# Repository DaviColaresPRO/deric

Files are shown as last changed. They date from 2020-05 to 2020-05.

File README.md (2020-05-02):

# deric - Desenvolvimento Experimental de Física Colaborativo
Sabe-se que não é fácil introduzir os jovens no mundo científico, mas existem maneiras de facilitar esse processo. Uma delas é a participação em olimpíadas científicas, e um bom exemplo é a OBF (Olimpíada Brasileira de Física). Em sua última fase, a OBF conta com uma prova teórica e uma prova experimental, cada uma valendo quase metade da nota final. Para conseguir um bom resultado, é essencial que o estudante vá bem em ambas. Porém, poucas são as escolas que possuem uma boa preparação em física experimental no país, pois é necessário contar com kits experimentais variados e com as instruções de como usá-los da maneira correta. É aí que o Projeto deric age, na democratização do acesso a equipamentos de laboratório e no ensino do uso eficiente destes. O projeto pretende alcançar o seu objetivo através da disponibilização na internet (no site GitHub) de guias de montagem e de utilização de kits experimentais de baixo custo, sendo o MDF a principal matéria-prima. Além disso, a plataforma GitHub permite que qualquer pessoa modifique e redistribua o material em diferentes versões, permitindo que os materiais sejam adaptados a diferentes demandas. Vários desses kits já foram usados no treinamento de uma escola de Fortaleza, contribuindo para o seu alto desempenho na OBF e na seletiva para as olimpíadas internacionais de física. Assim sendo, os kits se mostraram efetivos. Vale notar também que esses equipamentos podem ser usados para melhorar a didática em sala de aula, já que experimentos visuais facilitam o aprendizado.
- Projeto desenvolvido por Davi Colares: https://www.linkedin.com/in/davi-colares/, Davi Maciel: linkedin

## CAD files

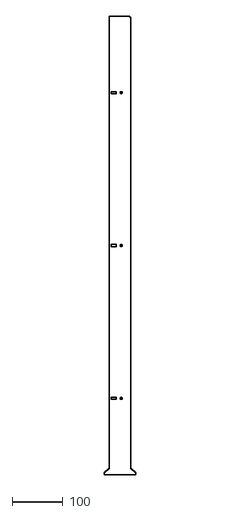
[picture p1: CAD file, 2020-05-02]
Experimentos de Física/Viscosímetro de Stokes/Arquivos dxf/Suporte Lateral.dxf
62.0 x 900.0

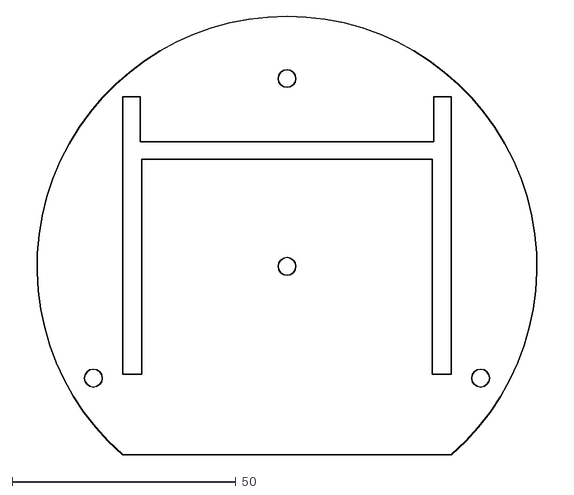
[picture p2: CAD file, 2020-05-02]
Experimentos de Física/Viscosímetro de Stokes/Arquivos dxf/Base do Suporte.dxf
121.0 x 98.0

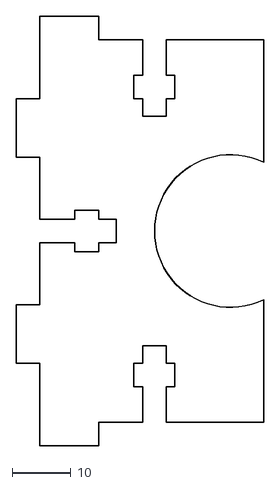
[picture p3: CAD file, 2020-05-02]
Experimentos de Física/Viscosímetro de Stokes/Arquivos dxf/Suporte da Lâmpada (x3).dxf
42.1 x 73.0

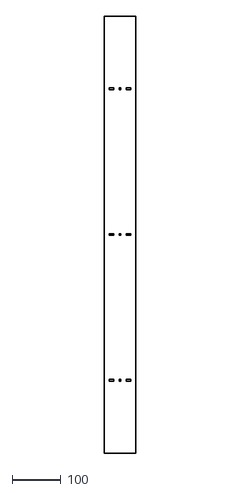
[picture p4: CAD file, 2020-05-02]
Experimentos de Física/Viscosímetro de Stokes/Arquivos dxf/Suporte Frontal.dxf
65.0 x 900.0

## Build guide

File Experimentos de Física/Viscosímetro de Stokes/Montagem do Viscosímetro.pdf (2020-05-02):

# Viscosímetro de Stokes

Davi Colares - Manual de Montagem

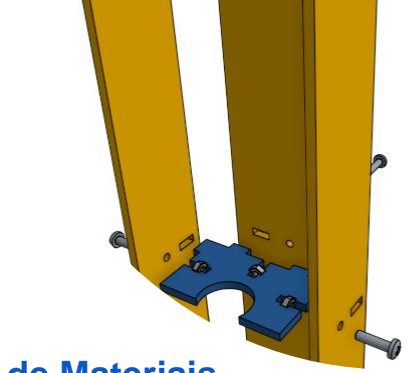
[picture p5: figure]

## Lista de Materiais

- Peças cortadas em MDF ou Acrílico
- 9 Parafusos M4X16
- 9 Roscas M4
- Uma base para fixar o modelo
- Supercola
- Lixa d’Agua
- Lâmpada de tudo
- Material de proteção
- Alicate
- 4 Parafusos para Madeira M4 (Opcionais)

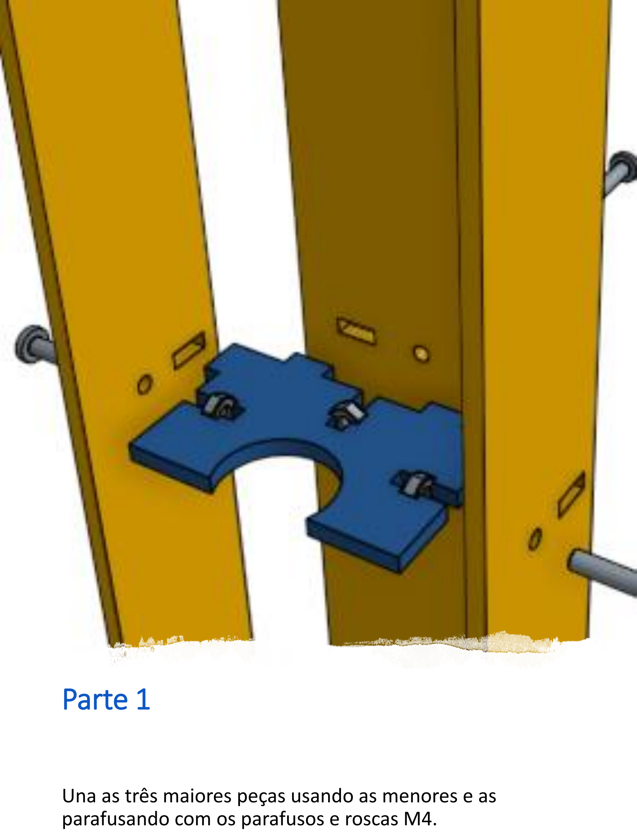
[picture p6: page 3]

## Parte 1

Una as três maiores peças usando as menores e as parafusando com os parafusos e roscas M4.

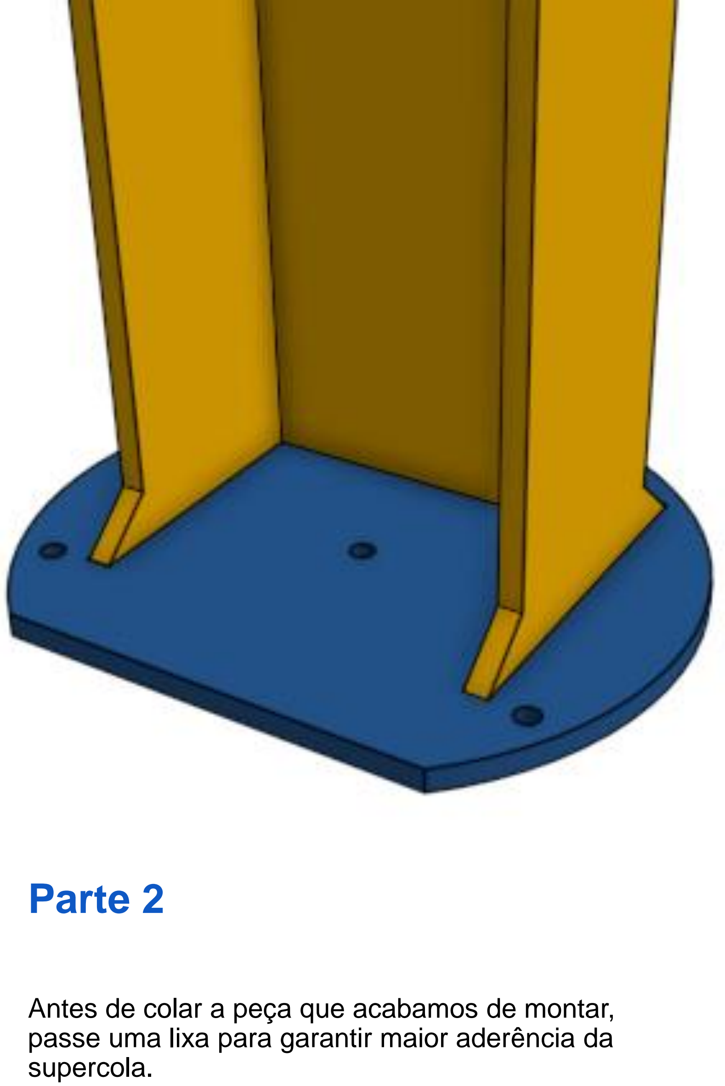
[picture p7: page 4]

## Parte 2

Antes de colar a peça que acabamos de montar, passe uma lixa para garantir maior aderência da supercola.

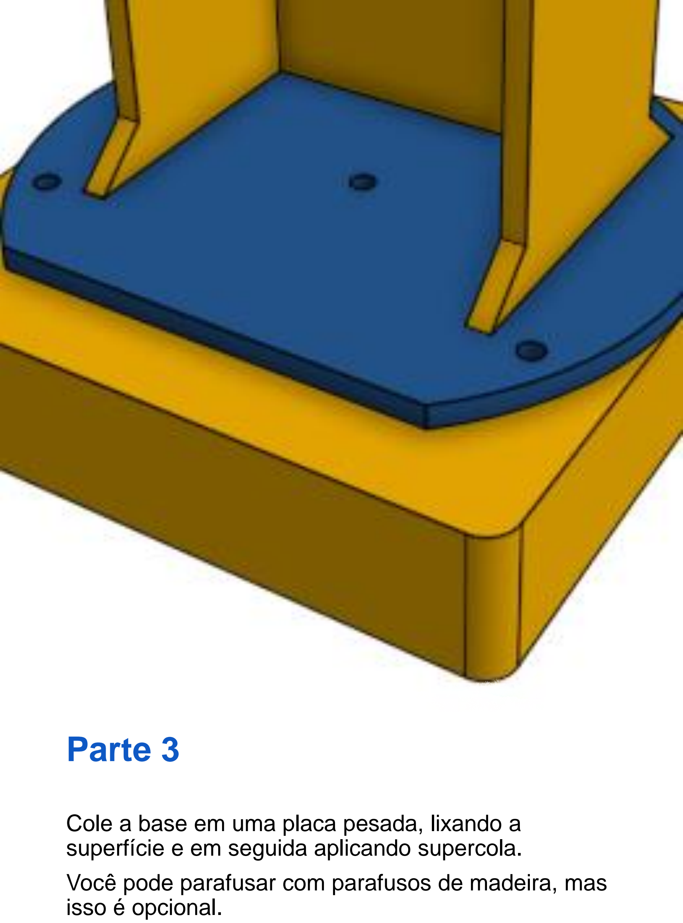
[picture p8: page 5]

## Parte 3

Cole a base em uma placa pesada, lixando a superfície e em seguida aplicando supercola.
Você pode parafusar com parafusos de madeira, mas isso é opcional.

## Suporte Pronto

## Parte 4

Usando material de proteção, iremos abrir o bulbo da lâmpada forçando com um alicate. Dentro de lâmpadas fluorescentes podem ser encontrados gases como argônio e vapor de mercúrio, sendo o último tóxico, além do material de segurança realize a abertura em local arejado.
Após abrir a lâmpada, retire seu conteúdo usando uma chave de fenda ou uma vareta, e lave o interior com água.
Tampe um dos lados usando uma rolha de silicone, ou algum outro material que impeça o vazamento do líquido que será usado na experimental.

## Parte 5

Com o tubo preparado e a cola seca, podemos encaixá-lo na base. Encaixe-o por cima, e nunca de frente, se você perceber que não está encaixando como deveria, então lixe os encaixes e tente novamente, esses tubos são sensíveis e não devem ser forçados contra o suporte.

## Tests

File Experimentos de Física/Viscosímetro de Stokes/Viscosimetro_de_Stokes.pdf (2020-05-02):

## MEDIDA DA VISCOSIDADE DA AGUA ´

Davi MacielaaaaaaaaVers˜ao: 20 de abril de 2020

### 1 Apresenta¸c˜ao e objetivos

Est´a pr´atica experimental tem como objetivo analisar a interferˆencia da viscosidade de um fluido no movimento de um corpo. Vamos estudar as consequˆencias e parˆametros relevantes num sistema simples: o viscos´ımetro de Stokes.

### 2 Materiais

- 1 Suporte para a lˆampada
- 1 Lˆampada preenchida com ´agua
- 1 Fita m´etrica
- 1 Cronˆometro
- Esferas de raios variados
- 1 Im˜a

### 3 Fundamenta¸c˜ao te´orica

A viscosidade ´e a resistˆencia que um fluido apresenta ao escoamento. Para ilustrar, pense numa garrafa com ´agua e numa garrafa com mel. Se vocˆe virar as duas de cabe¸ca pra baixo, ver´a que existe uma maior dificuldade de derramar mel do que derramar ´agua. Isso acontece por que o mel ´e mais viscoso do quˆe a ´agua. A seguir, vamos analisar como essa viscosidade influˆencia a queda vertical de uma esfera homogˆenea na ´agua. Para isso, iremos fazer uso da Lei de Stokes, que relaciona a for¸ca de fric¸c˜ao sentida pela esfera com seus parˆametros e com o meio, quando o n´umero de Reynolds ´e menor que 1. Essa lei ´e descrita pela seguinte f´ormula:

F~ = −6πrη~v,

onde:

F~ ´e a forca de fric¸c˜ao,
r ´e o raio da esfera,
η ´e o coeficiente de viscosidade do fluido, e
~v ´e a velocidade da esfera em rela¸c˜ao ao fluido.

Existem 3 for¸cas agindo na esfera enquanto ela cai na ´agua:

F

E

mg

Figura 1

onde:
F~ ´e a for¸ca de fric¸c˜ao
E~ ´e a for¸ca de empuxo, e m~g ´e o peso.

A 2a Lei de Newton fica:

m~a = m~g + F~ + E~ →

→ ma = mg − 6πrηv − ρaV g,

onde m e V s˜ao a massa e o volume da esfera, respectivamente, e ρa ´e a densidade da ´agua.
Sabendo a densidade ρ da esfera, temos:

m = ρV = ρ

4
3

πr³

Da´ı:

ma = (ρ − ρa)

4
3

πr³
g − 6πrηv.

A velocidade vai aumentando at´e que o lado direito da equa¸c˜ao acima tenda a zero, fazendo que a acelera¸c˜ao tenda a zero da mesma forma. No nosso experimento, podemos considerar que isso acontece bem r´apido, ou seja, vocˆe pode considerar que a esfera come¸ca um movimento uniforme poucos cent´ımetros abaixo da superf´ıcie da ´agua. Assim, a velocidade terminal ´e:

v = (ρ − ρa)

2g
9η

r

2

Com essa rela¸c˜ao em m˜aos e utilizando dados experimentais, podemos achar o coeficiente de viscosidade da ´agua. Podemos achar at´e mesmo o raio de uma esfera, se tivermos o coeficiente de viscosidade da ´agua.

### 4 Procedimentos experimentais

4.1

Utilizando os equipamentos fornecidos, levante dados de deslocamento por tempo de queda para cada esfera, lembrando de esperar que a esfera tenha entrado alguns cent´ımetros na ´agua antes de iniciar a contagem do cronˆometro. Fa¸ca isso 3 vezes para cada esfera e depois calcule a m´edia das velocidades terminais encontradas, que chamaremos de vm. Organize os dados em tabelas, n˜ao esquecendo de apresentar todos os erros e os m´etodos utilizados para os c´alculos destes.

4.2

Como estamos lidando com um tubo de raio finito, as paredes do mesmo ir˜ao influenciar no movimento das esferas e, consequentemente, devemos corrigir as velocidades obtidas ante de calcular a viscosidade. Essa corre¸c˜ao pode ser feita aproximadamente por uma simples multiplica¸c˜ao de cada velocidade obtida pelo fator de corre¸c˜ao:

K = 1 + 2, 4r/R,

onde r ´e o raio da respectiva esfera e R ´e o raio do tubo. Sabendo disso, apresente uma tabela com os valores de vm obtidos experimentalmente, os fatores de corre¸c˜ao, e as velocidades corrigidas vc. Os ´unicos erros que dever˜ao ser apresentados nessa tabela s˜ao os de vc.

-p´agina 1-

4.3

Construa um gr´afico de vm por r

2
e um de vc por r

2
, ambos na mesma folha de papel quadriculada. N˜ao esque¸ca de apresentar as barras de erro.

4.4

Atrav´es do coeficiente angular do gr´afico de vc por r

2
, determine o valor da viscosidade da ´agua com sua respectiva incerteza.

4.5

O valor encontrado na literatura para a viscosidade da ´agua ´e cerca de 1, 00 · 10⁻³ P a · s. O valor encontrado por vocˆe ´e pr´oximo do esperado? Se n˜ao, justifique.

N´umero de Reynolds: Re =

2ρvr
η

-p´agina 2-
